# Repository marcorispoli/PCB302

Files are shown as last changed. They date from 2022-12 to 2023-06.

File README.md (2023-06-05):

# PCB/22-302 - Compressor device controller (DiMoBIS)

## Descrizione

Scheda di controllo del dispositivo di compressione del mammografo Z190.

## Struttura cartelle

```text
pcb-22-302/     [pcb-22-302.git]
├── artifacts/
│   ├── archive/
│   ├── current/
│   │   ├── docs/
│   │   └── layout/
│   │       ├── drawings/
│   │       ├── gerbers/
│   │       └── pick&place/
│   ├── datasheets/
│   └── releases/
├── capture/
├── docs/
├── layout/
├── scripts/
└── spice/
```

- `artifacts` contiene tutti gli artefatti generati dal progetto ed eventuali risorse esterne.
  - `archive` contiene le versioni archiviate degli artefatti generati.
  - `current` contiene la versione corrente degli artefatti generati.
  - `datasheets` contiene la documentazione di alcuni componenti utilizzati nel progetto.
  - `releases` contiene i rilasci del progetto del master del PCB.
- `capture` contiene il progetto dello schematico.
- `docs` contiene la documentazione di progetto.
- `layout` contiene il progetto del layout del PCB.
- `scripts` contiene lo script di generazione della lista parti.
- `spice` contiene alcuni progetti di simulazione.

## Strumenti di sviluppo

- Lo schematico della scheda è sviluppato in **Cadence OrCAD Capture 17.4**.
- Il layout del PCB della scheda è sviluppato in **Cadence OrCAD Layout Plus 16.2**.

## Documentazione

- [Progettazione](docs/progettazione.md)
- [Schematico](artifacts/current/docs/SE22-302-0_r3.pdf)
- [Schematico (collaudo)](docs/collaudo-rev2.pdf)
- [Lista parti](artifacts/current/docs/LP22-302-0_r3.pdf)
- [Piano di montaggio](artifacts/current/layout/drawings/PM22-302-0.pdf)

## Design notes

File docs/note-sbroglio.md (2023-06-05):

# Note di sbroglio

*Ultima modifica: 31/05/2023*

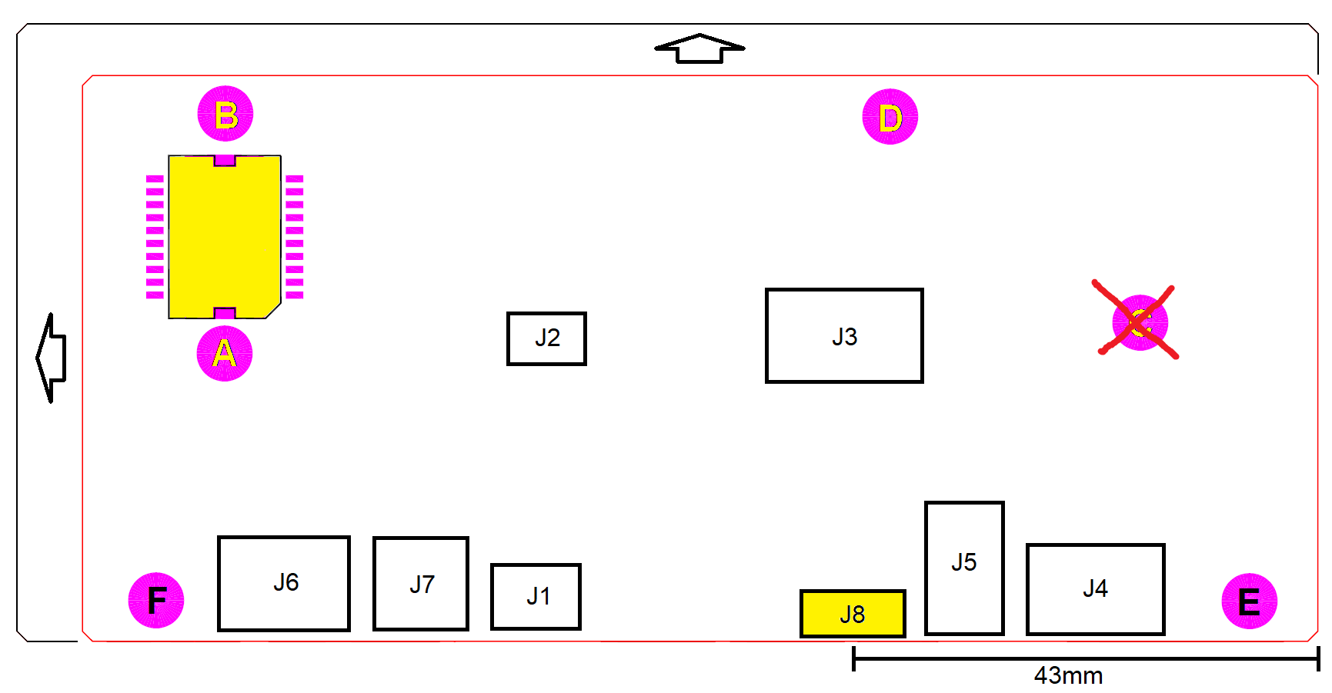
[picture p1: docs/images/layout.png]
layout


1. Il codice del circuito stampato è **CS/22-302-0**.

2. La struttura della scheda ricalca grosso modo quella della scheda 16-269-0. La serigrafia della nuova scheda sarà ruotata di 180° rispetto alla scheda 16-269-0.

3. Le dimensioni minime della scheda sono uguali a quelle della scheda 16-269-0, `121.3mm x 55.6mm` (contorno rosso), le dimensioni massime sono `130mm x 60mm` (contorno nero). L'estensione può avvenire verso sinistra e verso l'alto.

4. Il PCB ha spessore 1.6mm ed ha 4 strati.

5. La foratura della scheda 16-269-0 è rappresentata dai fori **A**, **B**, **C** e **D**. Nella nuova scheda verrà rimosso il foro **C** e si aggiungeranno i fori **E** e **F** posizionati lungo il bordo inferiore, ai lati dei connettori.

6. I connettori sono di seguito elencati:

    | Connettore | Etichetta | Tipo         | Descrizione                          |
    | -- | ------------- | ---------------- | ------------------------------------ |
    | J1 | `24VDC`       | [105311-1102]    | Alimentazione a 24V                  |
    | J2 | `SUPPLY_TEST` | [HEADER-3x2]     | Monitor alimentazioni scheda         |
    | J3 | `DEBUG`       | [61200621621]    | Interfaccia di programmazione        |
    | J4 | `HW_BUS`      | [105310-2210]    | Interfaccia Hardware Bus             |
    | J5 | `POSITION`    | [22-05-3031]     | Interfaccia  potenziometro posizione |
    | J6 | `MOTOR`       | [MC1,5/3-G-3,81] | Interfaccia motore                   |
    | J7 | `BRAKE`       | [MC1,5/2-G-3,81] | Interfaccia freno                    |
    | J8 | `PADDLE`      | [54548-1071]     | Interfaccia paddle                   |

    [105311-1102]: https://www.molex.com/pdm_docs/sd/1053111102_sd.pdf
    [61200621621]: https://www.we-online.com/catalog/datasheet/61200621621.pdf
    [105310-2210]: https://www.molex.com/pdm_docs/sd/1053101210_sd.pdf
    [22-05-3031]: https://www.molex.com/pdm_docs/sd/022053031_sd.pdf
    [MC1,5/3-G-3,81]: https://www.phoenixcontact.com/product/pdf/api/v1/MTgwMzI4MA?_realm=us&_locale=en-US&blocks=commercial-data%2Ctechnical-data%2Cdrawings
    [MC1,5/2-G-3,81]: https://www.phoenixcontact.com/product/pdf/api/v1/MTgwMzI3Nw?_realm=us&_locale=en-US&blocks=commercial-data%2Ctechnical-data%2Cdrawings
    [54548-1071]: https://www.molex.com/pdm_docs/sd/545482671_sd.pdf
    [HEADER-3x2]: https://www.molex.com/pdm_docs/sd/901310123_sd.pdf

7. I connettori **J1**, **J4**, **J5**, **J6**, **J7**, **J8** devono essere posizionati lungo il bordo inferiore della scheda.

8. Il connettore **J8** deve essere posizionato a 43mm (asse simmetria) dal bordo destro della scheda.

9. Il piano di massa **GND** deve essere solido e continuo, a meno eventualmente della net **CHASSIS_GND**.

10. I diodi TVS (**SMBJ\*A**, **SD05-\***) devono essere piazzati il più vicino possibile ai connettori associati.

11. La net **CHASSIS_GND**, (copper area?) deve essere posizionata lungo tutto il bordo inferiore e accogliere tutti gli anodi dei diodi TVS.

12. I fori **E** ed **F** devono essere connessi alla net **CHASSIS_GND** così come indicato nello schematico dai fori **MH1** e **MH2**. Il foro **MH1** sarà connesso a **GND** tramite **R6** il più vicino possibile al foro.

13. Riportare sulla serigrafia le etichette espresse dalla proprietà **COMMENT** dei componenti dello schematico, limitatamente ai connettori, ai testpoint e ai led. NON INCLUDERE LE PARENTESI QUADRE.

14. Piazzare i led sullo strato TOP.

## Modifiche sbroglio (schematico revisione 3)

[Collaudo revisione 2](./collaudo-rev2.pdf)

- [x] Portare i connettori **J6** (`MOTOR`) e **J7** (`BRAKE`) a filo del bordo scheda. Spostare le etichette all'interno.
- [x] Scambiare di posto **DL12** e **DL13**.
- [x] Riportare in visibilità l'etichetta di **R41**, coperta dal solder mask di **U11**.
- [x] Inserito **R78** sulla net `CURRENT_SENSOR`, nella pagina `ANALOG`.
- [x] Inserito **R79** in parallelo a **C37**, nella pagina `MOTOR`.
- [x] Corretto il simbolo sullo schematico di **U12**.
- [x] Invertite le net sui pin `1` e `2` di **U12**.
- [x] Inserito il jumper **J9** in parallelo all'uscita di **U12**, nella pagina `MOTOR`.
- [x] Inserito **D29** in parallelo a **J7**, nella pagina `BRAKE`.
- [x] Disconnesso il pin `11` di **U13** e **U14** dalla net `CALIBRATION_ENA`, nella pagina `SAFETY1`.
- [x] Inseriti **D30** e **R80** sull'ingresso di **U16A**, nella pagina `SAFETY2`.
- [x] Sostituito il connettore **J8** con connettore da 12 pin anziché 10, nella pagina `PADDLE`.
- [x] Il codice `22-302-0` resta invariato.

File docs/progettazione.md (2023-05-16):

# PCB/22-302 - Progettazione

- [1. Requisiti](#1-requisiti)
  - [1.1. Alimentazione](#11-alimentazione)
  - [1.2. Elaborazione](#12-elaborazione)
  - [1.3. Comunicazione](#13-comunicazione)
  - [1.4. Azionamento](#14-azionamento)
  - [1.5. Gestione paddle](#15-gestione-paddle)
  - [1.6. Sicurezza](#16-sicurezza)
- [2. Implementazione](#2-implementazione)
  - [2.1. Dispositivi](#21-dispositivi)
    - [2.1.1. Motore](#211-motore)
    - [2.1.2. Freno di tenuta](#212-freno-di-tenuta)
    - [2.1.3. Sensore di forza](#213-sensore-di-forza)
    - [2.1.4. Potenziometro](#214-potenziometro)
  - [2.2. Connettori](#22-connettori)
  - [2.3. Alimentazione](#23-alimentazione)
  - [2.4. Processore](#24-processore)
    - [2.4.1. Revisione della scheda](#241-revisione-della-scheda)
  - [2.5. Comunicazione](#25-comunicazione)
    - [2.5.1. Interfaccia `HW_BUS`](#251-interfaccia-hw_bus)
    - [2.5.2. Interfaccia `PADDLE`](#252-interfaccia-paddle)
  - [2.6. Azionamento](#26-azionamento)
    - [2.6.1. Motore](#261-motore)
    - [2.6.2. Freno di tenuta](#262-freno-di-tenuta)
    - [2.6.3. Sensore di forza](#263-sensore-di-forza)
    - [2.6.4. Sensore di posizione](#264-sensore-di-posizione)
    - [2.6.5. Sensore di corrente](#265-sensore-di-corrente)
  - [2.7. Sicurezza](#27-sicurezza)
    - [2.7.1. Potenziometri](#271-potenziometri)
    - [2.7.2. Comparatori](#272-comparatori)
    - [2.7.3. Abilitazione della calibrazione](#273-abilitazione-della-calibrazione)
    - [2.7.4. Abilitazione del compressore](#274-abilitazione-del-compressore)
    - [2.7.5. Rilevazione della compressione](#275-rilevazione-della-compressione)
    - [2.7.6. Blocco della compressione](#276-blocco-della-compressione)
    - [2.7.7. Taglio dell'alimentazione del motore](#277-taglio-dellalimentazione-del-motore)
- [3. Documentazione](#3-documentazione)
  - [3.1. Componenti](#31-componenti)

## 1. Requisiti

Di seguito sono descritti tutti i requisiti a cui la progettazione della scheda PCB/22-302 è chiamata a soddisfare, così come sono stati definiti all'interno della documentazione qui sotto elencata:

- *Gantry Hardware Specification - Compressor Device*
- *Gantry Hardware Specification - Hardware Interfaces*

### 1.1. Alimentazione

La scheda PCB/22-302 riceve un'alimentazione in tensione continua a 24V direttamente dalla scheda servizi PCB/22-301, che ne garantisce la continuità tramite la funzione UPS.

### 1.2. Elaborazione

Le funzioni di controllo del compressore sono eseguite dalla scheda PCB/22-302 per mezzo di un microcontrollore a 32 bit, modello SAME51J20A, prodotto da Microchip, avente core ARM Cortex-M4 a 120MHz, e package TQFP a 64 pin.

### 1.3. Comunicazione

La scheda PCB/22-302 comunica con il sistema di elaborazione centrale, rappresentato dal *Gantry Control Unit*, per mezzo del *CAN Bus* a 1Mbps.

La scheda PCB/22-302 è inoltre connessa all'*Hardware Bus* proveniente dalla scheda PCB/22-305 (C-ARM Hub).

### 1.4. Azionamento

L'azionamento del compressore viene realizzato tramite il controllo di un motore a spazzole in corrente continua che movimenta il paddle di compressione, su un binario di scorrimento, per mezzo di una cinghia dentata.

Il controllo dell'azionamento è coadiuvato da un sensore di forza posto sul supporto del paddle e da un sensore potenziometrico che restituisce la posizione del carrello del paddle sul binario.

L'azionamento del compressore è comandato in vari modi:

- tramite comandi ricevuti dal *Gantry Control Unit* attraverso il *CAN Bus*;
- tramite appositi segnali dell'*Hardware Bus*;
- tramite interruttori incorporati nelle manopole per la compressione manuale ed integrate nel supporto del paddle.

### 1.5. Gestione paddle

Il paddle di compressione è un componente estraibile e sostituibile con diversi modelli. Il sistema deve conoscere se il paddle è presente e che tipo di paddle è installato.

L'elettronica di rilevamento e identificazione del paddle è situata sulla scheda PCB/22-306 (Paddle Device Board). Su tale scheda sono inoltre connessi il sensore di forza e i pulsanti di attivazione manuale integrati nelle manopole del compressore.

La scheda PCB/22-306 è connessa alla scheda PCB/22-302 e da questa riceve l'alimentazione.

### 1.6. Sicurezza

L'azionamento del motore del compressore deve tenere in conto l'informazione della pressione realizzata durante l'azionamento stesso.

La massima compressione realizzabile per via automatica, cioè eseguita dal firmware controllando il motore, è limitata a 200N. Tale limite deve essere garantito da un'opportuna elettronica, posta al di fuori del controllo del firmware, che impedisca ulteriori aumenti della pressione pur consentendo la decompressione.

Oltre l'azionamento automatico fino a un massimo di 200N, il sistema prevede l'intervento manuale per l'incremento della compressione fino a 300N. Anche questo secondo limite deve essere garantito dall'elettronica non controllata dal firmware e, in caso di violazione, deve provvedere al taglio completo della potenza dell'azionamento.

## 2. Implementazione

### 2.1. Dispositivi

#### 2.1.1. Motore

| Proprietà   | Valore                             |
| ----------- | ---------------------------------- |
| Produttore  | Soho Precision Machinery Co., Ltd. |
| Part number | `GBN50-4D-25068B-28Y-RC-RH`        |
| Codice MT   | MR-GBN50-4D-2                      |

- [SOHO homepage](http://sohomotor.com/index.html)
- [DC Gearmotors](../artifacts/datasheets/motore/soho/Compact-DC-Gearmotors-Product-Data-Sheet_v2.pdf)
- [7E4065B-28Y (DC Motor)](../artifacts/datasheets/motore/soho/7E4065.pdf)
- [GBN50 (Spur Gearhead)](../artifacts/datasheets/motore/soho/GBN50.pdf)

#### 2.1.2. Freno di tenuta

#### 2.1.3. Sensore di forza

| Proprietà   | Valore               |
| ----------- | -------------------- |
| Produttore  | TE Connectivity      |
| Part number | `FX293X-100A-0100-L` |
| Codice MT   | ???                  |

- [Product page](https://www.te.com/usa-en/product-CAT-FSE0006.html)
- [Datasheet](../artifacts/datasheets/sensore/te/FX29.pdf)

#### 2.1.4. Potenziometro

| Proprietà   | Valore         |
| ----------- | -------------- |
| Produttore  | Bourns         |
| Part number | `3590S-2-502L` |
| Codice MT   | ???            |

- [Product page](https://www.bourns.com/products/potentiometers/precision-pots-multiturn/product/3590)
- [Datasheet](../artifacts/datasheets/potenziometro/3590.pdf)

### 2.2. Connettori

| Connettore | Etichetta | Tipo         | Descrizione                          |
| -- | ------------- | ---------------- | ------------------------------------ |
| J1 | `24VDC`       | [105311-1102]    | Alimentazione a 24V                  |
| J2 | `SUPPLY_TEST` | [HEADER-3x2]     | Monitor alimentazioni scheda         |
| J3 | `DEBUG`       | [61200621621]    | Interfaccia di programmazione        |
| J4 | `HW_BUS`      | [105310-2210]    | Interfaccia Hardware Bus             |
| J5 | `POSITION`    | [22-05-3031]     | Interfaccia  potenziometro posizione |
| J6 | `MOTOR`       | [MC1,5/3-G-3,81] | Interfaccia motore                   |
| J7 | `BRAKE`       | [MC1,5/2-G-3,81] | Interfaccia freno                    |
| J8 | `PADDLE`      | [54548-1071]     | Interfaccia paddle                   |

[105311-1102]: https://www.molex.com/pdm_docs/sd/1053111102_sd.pdf
[61200621621]: https://www.we-online.com/catalog/datasheet/61200621621.pdf
[105310-2210]: https://www.molex.com/pdm_docs/sd/1053101210_sd.pdf
[22-05-3031]: https://www.molex.com/pdm_docs/sd/022053031_sd.pdf
[MC1,5/3-G-3,81]: https://www.phoenixcontact.com/product/pdf/api/v1/MTgwMzI4MA?_realm=us&_locale=en-US&blocks=commercial-data%2Ctechnical-data%2Cdrawings
[MC1,5/2-G-3,81]: https://www.phoenixcontact.com/product/pdf/api/v1/MTgwMzI3Nw?_realm=us&_locale=en-US&blocks=commercial-data%2Ctechnical-data%2Cdrawings
[54548-1071]: https://www.molex.com/pdm_docs/sd/545482671_sd.pdf
[HEADER-3x2]: https://www.molex.com/pdm_docs/sd/901310123_sd.pdf

### 2.3. Alimentazione

L'alimentazione viene fornita alla scheda tramite il connettore **J1** (`24VDC`):

| Pin | Segnale | Descrizione         |
| - | -------- | -------------------- |
| 1 | `IN_24V` | Ingresso linea a 24V |
| 2 | `IN_0V`  | Ingresso linea a 0V  |

L'alimentazione in ingresso viene posta in protezione tramite un fusibile **F1** da 5A, e filtrata con il filtro EMI **FLT1**, fornendo alla scheda la net di alimentazione `24V`.

A partire dall'alimentazione `24V`, tramite il regolatore switching **U1** ([R-78E-1.0]), viene generata l'alimentazione `5V`, per una corrente fino a 1A.

Dall'alimentazione `5V`, tramite il regolatore lineare **U2** ([NCP1117]), viene generata l'alimentazione `3V3`, per una corrente fino a 1A.

Le tre alimentazioni fornite alla scheda sono riportate sul connettore **J2** (`SUPPLY_TEST`) per agevolarne il test. Un partitore con rapporto 1:12 e applicato all'alimentazione `24V` produce il segnale `SUPPLY_MONITOR` in ingresso al microcontrollore.

### 2.4. Processore

Di seguito l'elenco dei segnali gestiti dal processore **U3** ([SAME51J20A]):

| Segnale           | Tipo | Direzione | Descrizione                                                   |
| ----------------- | :-------: | :--: | ------------------------------------------------------------- |
| `SUPPLY_MONITOR`  | analogico | I    | Partitore 1:12 dell'alimentazione `24V`                       |
| `COMPRESSOR_ENA`  | digitale  | I    | Abilitazione del compressore dall'HW_BUS                      |
| `COMPRESSOR_UP`   | digitale  | I    | Comando di decompressione dall'HW_BUS                         |
| `COMPRESSOR_DOWN` | digitale  | I    | Comando di compressione dall'HW_BUS                           |
| `CALIBRATION_ENA` | digitale  | I    | Abilitazione della calibrazione dall'HW_BUS                   |
| `BRIDGE_IN1`      | digitale  | O    | Controllo dell'half bridge 1 del driver motore                |
| `BRIDGE_IN2`      | digitale  | O    | Controllo dell'half bridge 2 del driver motore                |
| `BRIDGE_ENB`      | digitale  | O    | Abilitazione del driver motore                                |
| `BRIDGE_ENB_FB`   | digitale  | I    | Feedback dell'abilitazione del driver motore                  |
| `BRAKE_OFF`       | digitale  | O    | Comando di distacco del freno di tenuta                       |
| `MOTOR_CUT`       | digitale  | O    | Comando di interruzione dell'alimentazione del motore         |
| `CURRENT_SENSOR`  | analogico | I    | Segnale del sensore di corrente del motore                    |
| `POSITION_SENSOR` | analogico | I    | Segnale del sensore di posizione                              |
| `FORCE_SENSOR`    | analogico | I    | Segnale del sensore di forza                                  |
| `FORCE_OVF1`      | digitale  | I    | Overflow della 1° soglia del sensore di forza                 |
| `FORCE_OVF2`      | digitale  | I    | Overflow della 2° soglia del sensore di forza                 |
| `FORCE_OVF3`      | digitale  | I    | Overflow della 3° soglia del sensore di forza                 |
| `CURRENT_OVF`     | digitale  | I    | Overflow della soglia del picco di corrente del motore        |
| `PADDLE_PRESENT`  | digitale  | I    | Segnale di presenza paddle                                    |
| `PADDLE_UP`       | digitale  | I    | Comando di decompressione dalla scheda PADDLE                 |
| `PADDLE_DOWN`     | digitale  | I    | Comando di compressione dalla scheda PADDLE                   |
| `UART_RX`         | digitale  | I    | Linea di ricezione dell'UART connessa con la scheda PADDLE    |
| `UART_TX`         | digitale  | O    | Linea di trasmissione dell'UART connessa con la scheda PADDLE |
| `CAN_RX`          | digitale  | I    | Linea di ricezione del CAN bus                                |
| `CAN_TX`          | digitale  | O    | Linea di trasmissione del CAN bus                             |
| `I2C_SDA`         | digitale  | I/O  | Linea dati del bus I2C                                        |
| `I2C_SCL`         | digitale  | O    | Linea di clock del bus I2C                                    |
| `ACTIVITY`        | digitale  | O    | Controllo del led **DL4** (`CPU`)                             |
| `HW_REVISION`     | analogico | I    | Revisione della scheda                                        |

#### 2.4.1. Revisione della scheda

L'informazione della revisione della scheda è fornita al microcontrollore dal partitore {**R12**, **R13**} le cui resistenze variano a passi di $500\Omega$ e la cui somma è fissa a $4k\Omega$. In tal modo:

$$ V_{HW\_REVISION} = 3.3V * \frac{n}{8} \space,\space con \space 0 \le n \le 8 $$

### 2.5. Comunicazione

La scheda PCB/22-302 comunica con l'esterno attraverso i connettori **J4** (`HW_BUS`) e **J8** (`PADDLE`).

#### 2.5.1. Interfaccia `HW_BUS`

Il connettore **J4** fornisce le interfacce dell'hardware bus, propriamente detto, e del CAN Bus.

| Pin | Segnale        | Pin | Segnale     |
| --- | -------        | --- | ----------- |
| 1   | `HW_CAN_H`     | 6   | `HW_CAN_L`  |
| 2   | `HW_CAN_GND`   | 7   | nc          |
| 3   | `HW_CMP_ENA`   | 8   | `HW_CMP_UP` |
| 4   | `HW_CMP_DWN`   | 9   | `HW_CMP_ON` |
| 5   | `HW_CALIB_ENA` | 10  | `GND_HW`    |

Segue la descrizione dei segnali:

- `HW_CAN_H`     - \[I/O\] Linea dati alta del CAN bus
- `HW_CAN_L`     - \[I/O\] Linea dati bassa del CAN bus
- `HW_CAN_GND`   - Massa del CAN bus
- `HW_CMP_ENA`   - \[I\] Abilitazione dell'azionamento del compressore. E' utilizzato dal microcontrollore ma interviene anche direttamente sull'hardware di azionamento.
- `HW_CMP_UP`    - \[I\] Richiesta di decompressione. E' utilizzato dal solo microcontrollore.
- `HW_CMP_DWN`   - \[I\] Richiesta di compressione. E' utilizzato dal solo microcontrollore.
- `HW_CMP_ON`    - \[O\] Stato di compressione in essere. Viene attivato quando il sensore di forza rileva una forza superiore ad un'appropriata soglia. **Viene generato per via hardware**.
- `HW_CALIB_ENA` - \[I\] Abilitazione delle operazioni di calibrazione. Interviene direttamente sull'hardware di calibrazione.
- `GND_HW`       - Massa dell'hardware bus

I segnali `HW_CAN_H`, `HW_CAN_L` e `HW_CAN_GND` sono inoltrati verso il driver **U4** ([TJA1050T]) che fornisce al processore i segnali `CAN_TX` e `CAN_RX`.

I restanti segnali dell'hardware bus, di dinamica compresa in 5V, sono isolati otticamente, tramite **U5**, **U6**, **U7**, **U8** e **U9** ([TCMT1103] e [CPC1017N]), e accoppiati ai segnali della scheda `COMPRESSOR_ENA`, `COMPRESSOR_UP`, `COMPRESSOR_DOWN`, `CALIBRATION_ENA` e `FORCE_OVF1`,

Di seguito il dimensionamento delle polarizzazioni degli opto-isolatori.

- TCMT1103: $V_F = 1.2V$, $CTR = 100\% \div 200\%$ ($@ I_F = 10mA$)
- CPC1017N: $V_F = 1.2V$, $R_{ON} = 6.5\Omega$ ($@ I_F = 5mA$)

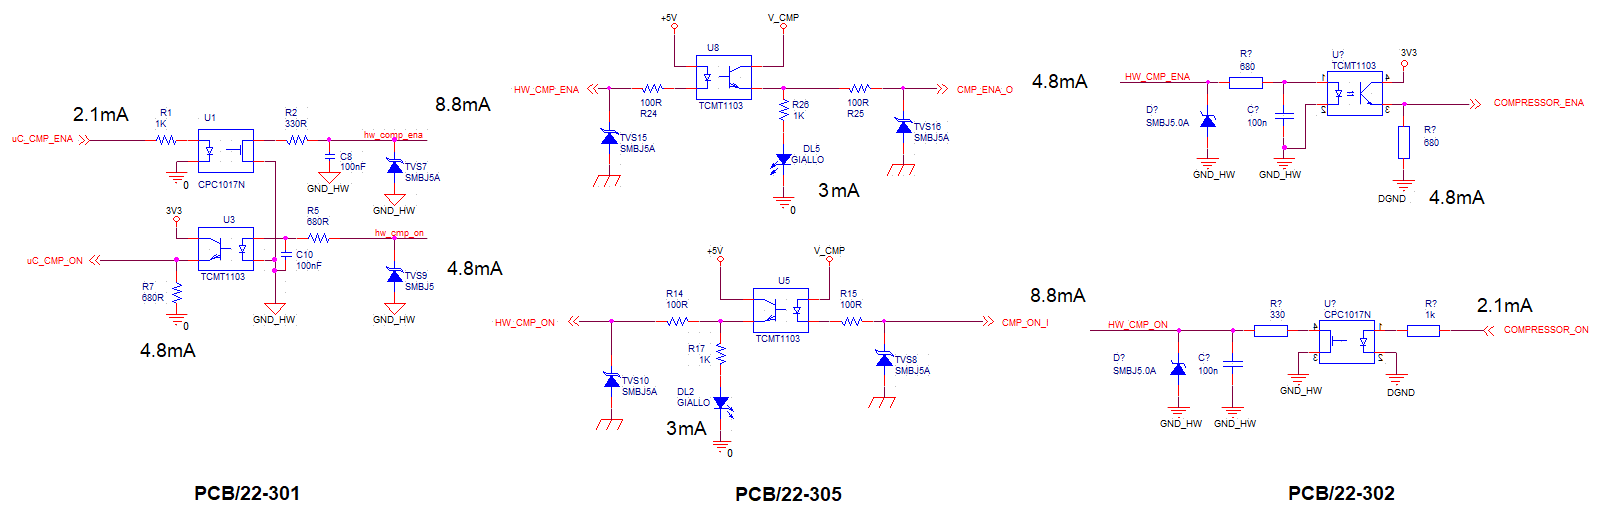
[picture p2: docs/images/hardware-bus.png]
hardware-bus


#### 2.5.2. Interfaccia `PADDLE`

Il connettore **J8** fornisce l'interfaccia verso la scheda PCB/22-306 (Paddle Device Board).

| Pin | Segnale        | Descrizione                                                        |
| --- | -------------- | ------------------------------------------------------------------ |
| 1   | `PAD_DVDD`     | Alimentazione a 5V della sezione digitale della scheda PCB/22-306  |
| 2   | `PAD_DGND`     | Massa della sezione digitale della scheda PCB/22-306               |
| 3   | `PAD_RX`       | \[O\] Linea di ricezione del lettore RFID                          |
| 4   | `PAD_TX`       | \[I\] Linea di trasmissione del lettore RFID                       |
| 5   | `PAD_PRESENT`  | \[I\] Presenza del paddle                                          |
| 6   | `PAD_UP`       | \[I\] Comando di decompressione                                    |
| 7   | `PAD_DOWN`     | \[I\] Comando di compressione                                      |
| 8   | `PAD_AVDD`     | Alimentazione a 5V della sezione analogica della scheda PCB/22-306 |
| 9   | `PAD_AGND`     | Massa della sezione analogica della scheda PCB/22-306              |
| 10  | `PADDLE_FORCE` | \[A\] Sensore di forza                                             |

I segnali digitali dell'interfaccia sono controllati nei loro fronti di salita allo scopo di limitare le emissioni attraverso il cablaggio verso la scheda PCB/22-306. A tale scopo le uscite sono filtrate attraverso un passa-basso RC con costante di tempo pari a 10us, mentre gli ingressi sono applicati al driver **U17** ([SN74HCS365]) con funzione di trigger di Schmidt al fine di ripristinare una veloce transizione dei segnali inoltrati verso il processore. La stessa procedura dovrà essere adottata sull'altro lato del cablaggio, cioè sulla scheda PCB/22-306.

### 2.6. Azionamento

L'azionamento del compressore viene realizzato per il tramite di un motore a spazzole in corrente continua controllato dal processore **U3** usando le informazioni fornite dai sensori di forza, di posizione e di corrente. In fase si arresto il motore è bloccato da un freno di tenuta.

#### 2.6.1. Motore

Il connettore **J6** (`MOTOR`) connette il motore al driver **U11** ([L6205PD]):

| Pin | Segnale | Descrizione             |
| --- | ------- | ----------------------- |
| 1   | `MOT1`  | Terminale 1 del motore  |
| 2   | -       | -                       |
| 3   | `MOT2`  | Terminale 2 del motore  |

Il driver **U11** contiene due ponti H completi (**A** e **B**) ed è configurato in modo che i semi-ponti del ponte **A** sono collegati in parallelo tra loro; lo stesso vale per il ponte **B**.

In tal modo il driver **U11** fornisce un ponte H completo con le seguenti caratteristiche:

- $R_{DS(ON)}$ : $0.15\Omega$
- Max RMS load current : $2.8A$
- OCD threshold : $5.6A$

I limiti di corrente corrispondono a quelli del singolo ponte H, ma la resistenza equivalente è dimezzata, consentendo una minore dissipazione di potenza.

Il modello di dissipazione è rappresentato dalla relazione

$$\ P_D = 2 \cdot R_H \cdot I_H^2 $$

dove

- $R_H$ rappresenta la resistenza equivalente del semi-ponte, comprensiva della quota di dissipazione dinamica, che ha un valore di circa $1.25\Omega$.
- $I_H$ rappresenta la corrente nel semi-ponte.

Ipotizzando una corrente massima nel motore pari a $I_{M,max}=1.5A$, la corrente in ciascun semi-ponte è pari alla metà di tale corrente, perciò

$$ P_{D,max} = 2 \cdot 1.25\Omega \cdot \left(\frac{1.5A}{2}\right)^2 = 1.4W $$

Il driver **U11** è provvisto di una piastrina di dissipazione (slug) nella faccia inferiore del contenitore. La resistenza termica tra giunzione e ambiente $R_{th,j-amb}$ può essere considerata compresa tra i valori:

- $30°C/W$ con lo slug saldato sul top e connesso da 16 vie al piano di massa, senza ulteriori aree di dissipazione.
- $62°C/W$ con lo slug non saldato.

La dissipazione della potenza massima $P_{M,max}$ comporta un innalzamento della temperatura di giunzione, rispetto all'ambiente, pari a:

$$ 42°C \lt \Delta T_{j-amb} \lt 87°C $$

comunque compatibile con i limiti del dispositivo.

Il driver **U11** è controllato dal processore per mezzo dei seguenti segnali:

| Segnale         | Descrizione                           |
| --------------- | ------------------------------------- |
| `BRIDGE_ENB_S`  | Abilitazione del driver               |
| `BRIDGE_ENB_FB` | Feedback dell'abilitazione del driver |
| `BRIDGE_IN1`    | Controllo del semi-ponte 1            |
| `BRIDGE_IN2`    | Controllo del semi-ponte 2            |

Il driver **U11** implementa la protezione contro la sovraccorrente. In caso di superamento della soglia $I_{OCD}$, l'abilitazione del driver viene forzata a massa, interrompendo l'alimentazione del motore. Il segnale `BRIDGE_ENB_FB` segnala tale evenienza al processore.

#### 2.6.2. Freno di tenuta

Il freno di tenuta resta bloccato fintanto che non viene alimentato. Il processore provvede a fornirgli la necessaria alimentazione tramite il segnale `BRAKE_OFF_S` che attiva il transistor **Q11**, sbloccando così il motore del compressore.

#### 2.6.3. Sensore di forza

Il sensore di forza è montato sulla scheda PCB/22-306 e fornisce la sua informazione attraverso l'interfaccia `PADDLE`. Il segnale `PADDLE_FORCE` fornito dal sensore ha una dinamica compresa tra 0.5V e 4.5V per valori della forza misurata compresi tra 0N e 500N.

Il segnale viene applicato ad un inseguitore di tensione e ridotto da un partitore con rapporto 2:3 per fornire al processore il segnale `FORCE_SENSOR`, la cui dinamica risulta quindi compresa tra 0.33V e 3V.

#### 2.6.4. Sensore di posizione

Il sensore di posizione è realizzato attraverso un potenziometro multigiri alimentato a 5V. Il segnale proveniente dal potenziometro viene applicato ad un inseguitore di tensione e ridotto da un partitore con rapporto 2:3 per fornire al processore il segnale `POSITION_SENSOR` avente dinamica compresa tra 0V e 3V.

#### 2.6.5. Sensore di corrente

Il sensore di corrente restituisce l'informazione della corrente che scorre all'interno del motore. Tale misura è utile a verificare l'informazione proveniente dal sensore di forza. Essendo infatti la coppia esercitata dal motore strettamente legata alla corrente che in esso scorre, il sensore di corrente rappresenta una preziosa ridondanza per il sensore di forza.

La misura parte dalla tensione `BRIDGE_SENS` presente ai capi della resistenza **R41** da $0.1\Omega/2W$, posta in serie al ponte H realizzato dal driver **U11** e collegata a massa.

Per una corrente massima di $I_{M,max}=1.5A$ la massima caduta di tensione su **R41** corrisponde a $V_{BRIDGE\_SENS,max}=150mV$, inoltre la massima dissipazione sarebbe $P_{R1,max}=225mW$, per cui una resistenza di $0.5W$ sarebbe stata sufficiente.

Il segnale `BRIDGE_SENS` viene filtrato (passa-basso RC con $\tau=100ns$) e amplificato con guadagno 10 per fornire al processore il segnale `CURRENT_SENSOR` avente massima dinamica di 1.5V.

Il segnale `CURRENT_SENSOR` viene inoltre applicato ad un rivelatore di picco la cui uscita `CURRENT_PEAK` viene utilizzata per la realizzazione di una sicurezza. Il rivelatore di picco presenta una costante di tempo per la carica pari a $\tau_c=10us$ e una costante di tempo per la scarica pari a $\tau_s=4ms$.

### 2.7. Sicurezza

Nella scheda sono implementate un numero di misure di sicurezza volte a ridurre l'impatto di eventuali condizioni di anomalia dovute principalmente a malfunzionamenti del firmware in esecuzione sul processore. A tale scopo queste sicurezze sono realizzate tramite soluzioni puramente hardware senza il coinvolgimento del processore.

Le sicurezze implementate sono governate essenzialmente dalle abilitazioni provenienti dall'hardware bus e da appositi comparatori che mettono a confronto le informazioni di forza e di corrente con soglie opportunamente configurate tramite potenziometri.

#### 2.7.1. Potenziometri

I potenziometri digitali **U13** e **U14** forniscono quattro soglie di tensione `VREF1`, `VREF2`, `VREF3` e `VREF4` comprese tra 0V e 3.3V.

Tali potenziometri sono controllati dal processore tramite il bus I2C. Di seguito sono indicati gli indirizzi sul bus dei due dispositivi:

| Dispositivo | Indirizzo bus I2C |
| --- | ---------- |
| U13 | `0101000b` |
| U14 | `0101001b` |

#### 2.7.2. Comparatori

Sulla scheda sono implementati quattro comparatori con isteresi. Tre di essi mettono a confronto il segnale `FORCE_SENSOR` con le soglie `VREF1`, `VREF2` e `VREF3` fornendo i segnali `FORCE_OVF1`, `FORCE_OVF2` e `FORCE_OVF3`. Il quarto comparatore confronta il segnale `CURRENT_PEAK` con la quarta soglia `VREF4` restituendo il segnale `CURRENT_OVF`.

I comparatori sono configurati per esprimere un'isteresi pari a 33mV, cioè pari a 1/100 della dinamica di alimentazione.

Di seguito la raffigurazione di un comparatore non invertente con isteresi:

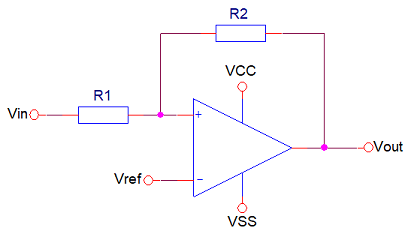
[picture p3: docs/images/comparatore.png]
comparatore


A causa della reazione positiva si hanno due configurazioni stabili equivalenti:

1. La tensione sull'ingresso non invertente $V^+$ dell'opamp è **superiore** alla tensione di riferimento $V_{ref}$, comportando in uscita dell'opamp una tensione pari a $V_{CC}$.
2. La tensione sull'ingresso non invertente $V^+$ dell'opamp è **inferiore** alla tensione di riferimento $V_{ref}$, comportando in uscita dell'opamp una tensione pari a $V_{SS}$.

Di seguito gli schemi equivalenti delle due configurazioni:

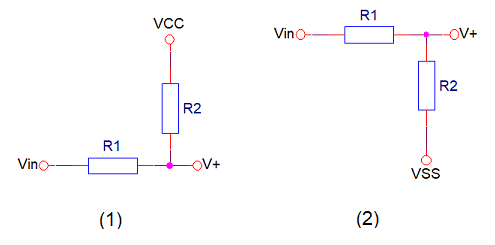
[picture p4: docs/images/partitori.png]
partitori


Il passaggio tra le due configurazioni si ha quando $V_{in}$ è tale che $V^+=V_{ref}$.

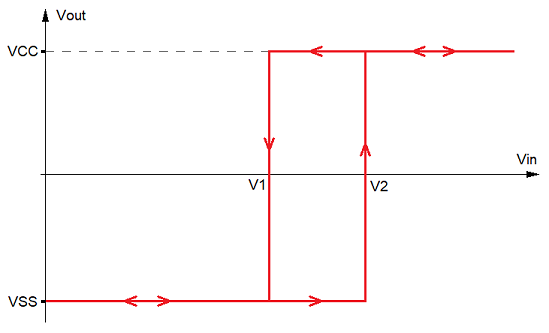
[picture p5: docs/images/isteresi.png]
isteresi


Dalla prima configurazione, posto $V_{in}=V_1$, si ha:

$$ V^+ = V_{ref} $$

$$ V_1 + (V_{CC} - V_1) \frac{R_1}{R_1 + R_2} = V_{ref} $$

mentre dalla seconda configurazione, posto $V_{in}=V_2$, si ha:

$$ V^+ = V_{ref} $$

$$ V_{SS} + (V_2 - V_{SS}) \frac{R_2}{R_1 + R_2} = V_{ref} $$

Semplificando rispetto a $V_{ref}$ si ottiene:

$$ V_1 + (V_{CC} - V_1) \frac{R_1}{R_1 + R_2} = V_{SS} + (V_2 - V_{SS}) \frac{R_2}{R_1 + R_2} $$

$$ V_1(R_1 + R_2) + (V_{CC} - V_1)R_1 = V_{SS}(R_1 + R_2) + (V_2 - V_{SS})R_2 $$

$$ V_1R_1 + V_1R_2 + V_{CC}R_1 - V_1R_1 = V_{SS}R_1 + V_{SS}R_2 + V_2R_2 - V_{SS}R_2 $$

$$ V_1R_2 + V_{CC}R_1 = V_{SS}R_1 + V_2R_2 $$

$$ (V_{CC} - V_{SS})R_1 = (V_2 - V_1)R_2 $$

La larghezza di isteresi è quindi pari a:

$$ \Delta V = V_2 - V_1 = (V_{CC} - V_{SS})\frac{R_1}{R_2} $$

#### 2.7.3. Abilitazione della calibrazione

I potenziometri digitali hanno memoria non volatile e devono essere programmati in una apposita procedura di calibrazione. Allo scopo di impedire indebiti accessi da parte del processore durante il normale funzionamento applicativo, il segnale `CALIBRATION_ENA` fornito dall'interfaccia `HW_BUS` controlla l'accesso ai potenziometri. Se infatti tale segnale non è attivo, è attiva la protezione contro la scrittura dei dispositivi ($\overline{WP}=low$). Inoltre se `CALIBRATION_ENA` è inattivo, la linea `I2C_SCL` è forzata a massa tramite i transistor **Q12** e **Q13** (pagina SAFETY1).

#### 2.7.4. Abilitazione del compressore

Il controllo del motore e del freno di tenuta da parte del processore viene abilitato tramite il segnale `COMPRESSOR_ENA` proveniente dall'interfaccia `HW_BUS`. Se infatti tale segnale è basso i segnali `BRIDGE_ENB_S` e `BRAKE_OFF_S` sono forzati a massa tramite i transistor **Q14**, **Q15** e **Q16** (pagina SAFETY3).

#### 2.7.5. Rilevazione della compressione

La rilevazione di compressione in corso viene eseguita tramite la comparazione del segnale `FORCE_SENSOR` e la soglia `VREF1` opportunamente calibrata (pagina SAFETY2). Il segnale di uscita del comparatore `FORCE_OVF1` viene applicato al terminale `HW_CMP_ON` dell'interfaccia `HW_BUS` (pagina HARDWARE BUS).

#### 2.7.6. Blocco della compressione

La compressione gestita da firmware è limitata al raggiungimento dei 200N di forza. Una volta raggiunto tale valore il driver del motore viene bloccato nel verso della compressione ma resta attivo nel verso della decompressione.

Il raggiungimento del limite dei 200N viene rilevato tramite la comparazione del segnale `FORCE_SENSOR` e la soglia `VREF2` opportunamente calibrata (pagina SAFETY2). Il segnale di uscita del comparatore `FORCE_OVF2` viene applicato ai transitor **Q17** e **Q18** che forzano il segnale `BRIDGE_IN1_S` a 3.3V. In questa maniera il semi-ponte 1 del driver **U11** risulta bloccato nella accensione del lato alto non permettendo ulteriori azionamenti del motore nel verso della compressione (SAFETY3).

> Il cablaggio del motore sul connettore **J6** deve essere disegnato in maniera che il blocco del semi-ponte 1 effettivamente impedisca il movimento del motore nel verso della compressione e non il contrario.

#### 2.7.7. Taglio dell'alimentazione del motore

Come detto la compressione automatica è limitata a 200N, ma è consentita un'ulteriore compressione, eseguita manualmente su apposite manopole installate sul supporto del paddle. La compressione manuale è a sua volta limitata a 300N. Nel caso che fosse superato tale limite, l'alimentazione del motore sarebbe interrotta.

Anche qui, il raggiungimento del limite dei 300N viene rilevato tramite la comparazione del segnale `FORCE_SENSOR` e la soglia `VREF3` opportunamente calibrata (pagina SAFETY2). Il segnale di uscita del comparatore `FORCE_OVF3` viene applicato al circuito di interruzione dell'alimentazione del motore.

Il circuito di interruzione è implementato tramite il relè a stato solido **U12** ([CPC1916Y]) pilotato da un multi-vibratore bistabile composto dai transistor **Q8** e **Q9** (pagina MOTOR).

All'accensione della scheda, il multi-vibratore è forzato nello stato attivo tramite il condensatore **C37**. Esso viene disattivato dal segnale `FORCE_OVF3` tramite il transistor **Q6**, spegnendo il relè **U12** e disalimentando il motore. Per la riattivazione del multi-vibratore è necessario spegnere e riaccendere la scheda.

## 3. Documentazione

### 3.1. Componenti

**Optoelettronici**:

- Opto-isolatore : [TCMT1103]
- Relè stato solido : [CPC1017N]
- Relè stato solido : [CPC1916Y]

[TCMT1103]: https://www.vishay.com/docs/83510/tcmt1100.pdf
[CPC1017N]: https://www.ixysic.com/home/pdfs.nsf/www/CPC1017N.pdf/$file/CPC1017N.pdf
[CPC1916Y]: https://www.ixysic.com/home/pdfs.nsf/www/CPC1916Y.pdf/$file/CPC1916Y.pdf

**Attivi**:

- Diodo piccoli segnali : [1N4148WT]
- Diodo TVS 600W : [SMBJ5.0A, SMBJ5.0CA, SMBJ30A, SMBJ30CA][SMBJ]
- Diodo TVS 450W : [SD05-01FTG][SD05]
- Diodo LED giallo : [APT2012YC]
- Diodo LED verde : [APT2012SGC]
- Diodo LED blu : [APT2012QBC/D]
- Diodo LED rosso : [APT2012EC]
- Transistor N-MOSFET 220mA : [BSS138]
- Transistor N-MOSFET 1.3A : [ZXMS6004FF]
- Transistor P-MOSFET 180mA : [BSS84]

[1N4148WT]: https://www.diodes.com/assets/Datasheets/1N4148WT.pdf
[SMBJ]: https://www.littelfuse.com/~/media/electronics/datasheets/tvs_diodes/littelfuse_tvs_diode_smbj_datasheet.pdf.pdf
[SD05]: https://www.littelfuse.com/~/media/electronics/datasheets/tvs_diode_arrays/littelfuse_tvs_diode_array_sd_datasheet.pdf.pdf
[APT2012YC]: https://www.kingbrightusa.com/images/catalog/SPEC/APT2012YC.pdf
[APT2012SGC]: https://www.kingbrightusa.com/images/catalog/SPEC/APT2012SGC.pdf
[APT2012QBC/D]: https://www.kingbrightusa.com/images/catalog/SPEC/APT2012QBC-D.pdf
[APT2012EC]: https://www.kingbrightusa.com/images/catalog/SPEC/APT2012EC.pdf
[BSS138]: https://www.onsemi.com/pdf/datasheet/bss138-d.pdf
[BSS84]: https://www.onsemi.com/pdf/datasheet/bss84-d.pdf
[ZXMS6004FF]: https://www.diodes.com/assets/Datasheets/ZXMS6004FF.pdf

**Passivi**:

- Bobina d'arresto : [DLW32SH101XF2L]
- Fusibile : [SMD050F-2]
- Ferrite : [BLM18BD102SN1D]
- Quarzo : [ECS-.327-12.5-16-TR3]

[DLW32SH101XF2L]: https://www.murata.com/products/productdata/8804914298910/QFLC9127.pdf
[SMD050F-2]: https://www.littelfuse.com/~/media/electronics/product_specifications/resettable_ptcs/littelfuse_ptc_smd050f_2_product_specification.pdf.pdf
[BLM18BD102SN1D]: https://www.murata.com/en-us/products/productdata/8796738650142/ENFA0003.pdf
[ECS-.327-12.5-16-TR3]: https://ecsxtal.com/store/pdf/ECX-16.pdf

**Integrati**:

- Driver CAN bus : [TJA1050T]
- Driver motore : [L6205PD]
- CPU : [SAME51J20A]
- Regolatore 5V : [R-78E-1.0]
- Regolatore 3.3V : [NCP1117]
- Amplificatore operazionale : [MCP6004]
- Potenziometro digitale : [MCP4661]
- Driver trigger di Schmidt : [SN74HCS365]

[TJA1050T]: https://www.nxp.com/docs/en/data-sheet/TJA1050.pdf
[L6205PD]: https://www.st.com/content/ccc/resource/technical/document/datasheet/group1/7f/8a/6c/96/c8/24/49/f6/CD00002345/files/CD00002345.pdf/jcr:content/translations/en.CD00002345.pdf
[SAME51J20A]: https://ww1.microchip.com/downloads/en/DeviceDoc/SAM_D5x_E5x_Family_Data_Sheet_DS60001507G.pdf
[R-78E-1.0]: https://recom-power.com/pdf/Innoline/R-78E-1.0.pdf
[NCP1117]: https://www.onsemi.com/pdf/datasheet/ncp1117-d.pdf
[MCP6004]: https://ww1.microchip.com/downloads/en/DeviceDoc/MCP6001-1R-1U-2-4-1-MHz-Low-Power-Op-Amp-DS20001733L.pdf
[MCP4661]: https://ww1.microchip.com/downloads/aemDocuments/documents/OTH/ProductDocuments/DataSheets/22107B.pdf
[SN74HCS365]: https://www.ti.com/lit/ds/symlink/sn74hcs365.pdf

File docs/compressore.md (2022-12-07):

# Struttura compressore

La struttura del compressore può essere così rappresentata:

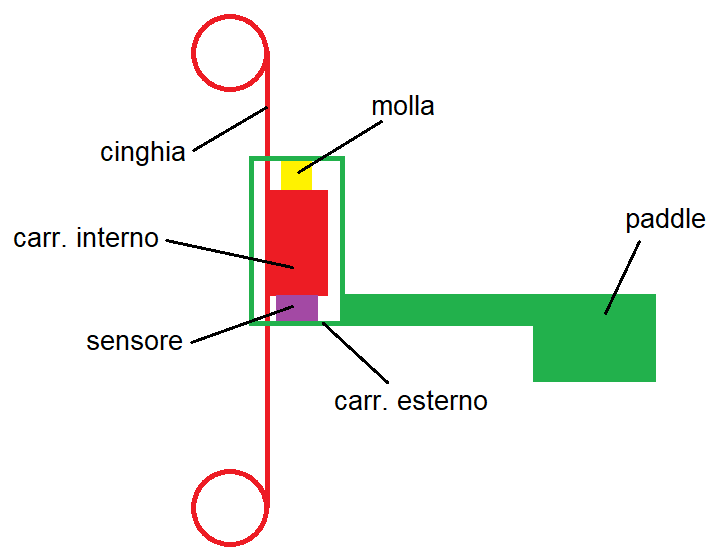
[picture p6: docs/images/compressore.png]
compressore


1. Il paddle è solidale al carrello esterno che si muove su due binari paralleli e verticali.
2. All'interno del carrello esterno, il carrello interno scorre attraverso due scanalature ricavate nel carrello esterno, in direzione parallela a quella del carrello esterno.
3. Il carrello interno è solidale alla cinghia azionata dal motore.
4. Nella parte inferiore del carrello interno è montato il sensore di pressione.
5. Nella parte superiore del carrello interno è montata una molla.
6. La molla controbilancia il peso dell'assieme verde (carrello esterno + paddle) che altrimenti, con il compressore sollevato, cadrebbe verso il basso distaccandosi dal sensore di pressione.

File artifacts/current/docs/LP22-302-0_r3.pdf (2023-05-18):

PCB/22-302-0 - Lista parti - rev. 3

Revisione | Data | Autore | Descrizione
1 | 07/12/2022 | LN | - Prima emissione.
2 | 07/03/2023 | LN | - Modificati i diodi D4, D5, D6, D7, D8, D9, D11, D13, D14, D21, D22, D23, D24, D25, D26, D27, D28 con part number SD05-01FTG, avente minor ingombro.
3 | 18/05/2023 | LN | - Inseriti i resistori R78, R79 e R80 - Inseriti i diodi D29, D30 - Inserito il jumper J9 - Modificato il connettore J8 con il part number 54548-1271 - Modificato il condensatore C37 con il valore 1uF - Modificato il regolatore U2 con il part number LD1117DT33 - Modificati gli optoisolatori U5, U7, U8, U9 con il part number TCMT1104 - Modificati i transistor Q2, Q17 con il part number BSS84

METALTRONICA S.p.a.

PCB/22-302-0 | Scheda di controllo del compressore (DiMoBIS)

Pagina 1 di 11

- Aggregato -
Pos. | Quantità | Riferimento | Valore | Descrizione | Produttore | Codice prod.
1 | 11 | C1, C2, C3, C4, C31, C33, C37, C41, C42, C44, C45 | 1u | Condensatore ceramico multistrato, 10%, 50V, SMD 0603
2 | 8 | C5, C6, C7, C8, C30, C39, C49, C50 | 10u | Condensatore ceramico multistrato, 10%, 50V, SMD 1210
3 | 2 | C9, C10 | 22p | Condensatore ceramico multistrato, 10%, 50V, SMD 0603
4 | 21 | C11, C12, C13, C14, C15, C16, C18, C22, C23, C24, C25, C26, C27, C29, C32, C40, C43, C46, C47, C48, C52 | 100n | Condensatore ceramico multistrato, 10%, 50V, SMD 0603
5 | 2 | C17, C19 | 4u7 | Condensatore ceramico multistrato, 10%, 50V, SMD 1210
6 | 2 | C20, C21 | 68p | Condensatore ceramico multistrato, 10%, 50V, SMD 0603
7 | 3 | C28, C34, C51 | 10n | Condensatore ceramico multistrato, 10%, 50V, SMD 0603
8 | 1 | C35 | 5n6 | Condensatore ceramico multistrato, 10%, 50V, SMD 0603
9 | 1 | C36 | 220n | Condensatore ceramico multistrato, 10%, 50V, SMD 0603
10 | 1 | C38 | 330u 35V | Condensatore elettrolitico alluminio, 20%, diam. 10mm, SMD
11 | 6 | DL1, DL2, DL3, DL10, DL11, DL13 | GREEN | LED verde, 20 mA, 2.2 V, SMD 0805 | Kingbright | APT2012SGC
12 | 1 | DL4 | BLUE | LED blu, 20 mA, 3,3 V, SMD 0805 | Kingbright | APT2012QBC/D
13 | 7 | DL5, DL6, DL7, DL8, DL18, DL19, DL20 | YELLOW | LED giallo, 20 mA, 2.1 V, SMD 0805 | Kingbright | APT2012YC
14 | 6 | DL9, DL12, DL14, DL15, DL16, DL17 | RED | LED rosso, 20 mA, 2 V, SMD 0805 | Kingbright | APT2012EC
15 | 5 | D1, D17, D18, D19, D20 | SMBJ30A | Diodo TVS 600W, 30V hold, 33.3V break, unidirezionale, SMD DO214AA | Littlefuse | SMBJ30A
16 | 3 | D2, D3, D29 | ES1A | Diodo rapido/ultra rapido, 50 V, 1 A, singolo, 920 mV, 15 ns, 30 A | Onsemi | ES1A
17 | 17 | D4, D5, D6, D7, D8, D9, D11, D13, D14, D21, D22, D23, D24, D25, D26, D27, D28 | SD05-01FTG | Diodo TVS 450W, 5V hold, 6V break, unidirezionale, SMD SOD323 | Littlefuse | SD05-01FTG
18 | 1 | D10 | SMBJ5.0CA | Diodo TVS 600W, 5V hold, 6.4V break, bidirezionale, SMD DO214AA | Littlefuse | SMBJ5.0CA
19 | 4 | D12, D15, D16, D30 | 1N4148WT | Diodo per piccoli segnali, 75V, 300mA, 1V, 4ns, SMD SOD-523F | Onsemi | 1N4148WT
20 | 1 | FLT1 | BNX002-11 | Filtro antirumore EMI, LC passa-basso 5° ordine, 2 canali, 10A, PTH | Murata | BNX002-11
21 | 1 | F1 | 0154005.DRT | Fusibile, azione ritardata, 5A, 125V, SMT con clip portafusibili | Littlefuse | 0154005.DRT
22 | 2 | F2, F3 | SMD050F-2 | Fusibile ripristinabile, 60V, I-hold 500mA, I-trip 1A, SMD | Littlefuse | SMD050F-2
23 | 1 | J1 | 105311-1102 | Connettore filo-scheda, serie Nano-Fit, 2 vie, passo 2.5mm, solder clip, verticale, PTH | Molex | 105311-1102
24 | 1 | J2 | HEADER-3x2 | Header maschio, 3x2 vie, passo 2.54mm, verticale, PTH | | <datasheet>
25 | 1 | J3 | 61200621621 | Connettore filo-scheda, serie WR-BHD, 3x2 vie, passo 2.54mm, verticale, PTH | Würth Elektronik | 61200621621
26 | 1 | J4 | 105310-2210 | Connettore filo-scheda, serie Nano-Fit, 5x2 vie, passo 2.5mm, verticale, PTH | Molex | 105310-2210
27 | 1 | J5 | 22-05-3031 | Connettore filo-scheda, serie KK254-7478, 3 vie, passo 2.54 mm, angolo retto, PTH | Molex | 22-05-3031
28 | 1 | J6 | MC1,5/3-G-3,81 | Morsettiera, strip maschio, 3.81mm, 3 vie, 8A, 160V, angolo retto, PTH | Phoenix Contact | MC1,5/3-G-3,81
29 | 1 | J7 | MC1,5/2-G-3,81 | Morsettiera, strip maschio, 3.81mm, 2 vie, 8A, 160V, angolo retto, PTH | Phoenix Contact | MC1,5/2-G-3,81
30 | 1 | J8 | 54548-1271 | Connettore FFC, 12 vie, passo 0.5mm, angolo retto, contatti in basso, SMD | Molex | 54548-1271
31 | 1 | J9 | HEADER-2 | Header maschio, 2 vie, passo 2.54mm, verticale, PTH
32 | 6 | L1, L2, L4, L5, L6, L7 | BLM18BD102SN1D | Perlina di ferrite, 1Kohm@100MHz, 200mA, SMD 0603 | Murata | BLM18BD102SN1D
33 | 1 | L3 | DLW32SH101XF2L | Filtro di modo comune per CAN Bus, 100uH@100kHz, 115mA, SMD 1210 | Murata | DLW32SH101XF2L

Pagina 2 di 11

- Aggregato -
Pos. | Quantità | Riferimento | Valore | Descrizione | Produttore | Codice prod.
36 | 4 | P1, P2, P3, P4 | 50k | Trimmer regolazione in testa 30 giri, 50K ohm, 10%, 0.5W | Bourns | 3296W-1-503LF
37 | 15 | Q1, Q3, Q4, Q5, Q6, Q7, Q8, Q9, Q10, Q12, Q13, Q14, Q15, Q16, Q18 | BSS138 | MOSFET canale N, 50V, 200mA, Vgs(th) 1.2V, SMD SOT-23-3 | Onsemi | BSS138
38 | 2 | Q2, Q17 | BSS84 | MOSFET canale P, -50V, -130mA, Vgs(th) -1,7V, SMD SOT-23-3 | Onsemi | BSS84
39 | 1 | Q11 | ZXMS6004FFTA | MOSFET canale N, protezioni OC OV OT, 60V, 1.3A, Vgs(th) 1.5V, SMD SOT-23-3 | Diodes Incorporated | ZXMS6004FFTA
40 | 1 | R1 | 22k | Resistore a film spesso, 1%, 1/10W, SMD 0603
41 | 4 | R2, R9, R10, R30 | 2k | Resistore a film spesso, 1%, 1/10W, SMD 0603
42 | 1 | R3 | 2k2 | Resistore a film spesso, 1%, 1/4W, SMD 1206
43 | 4 | R4, R20, R42, R47 | 330 | Resistore a film spesso, 1%, 1/10W, SMD 0603
44 | 10 | R5, R39, R40, R55, R56, R59, R62, R71, R72, R73 | 120 Resistore a film spesso, 1%, 1/10W, SMD 0603
45 | 1 | R6 | JUMPER | Resistore a film spesso, 1%, 1/8W, SMD 0805
46 | 20 | R7, R14, R33, R35, R44, R45, R46, R48, R49, R50, R65, R66, R67, R68, R74, R75, R76, R77, R78, R80 | 10k | Resistore a film spesso, 1%, 1/10W, SMD 0603
47 | 11 | R8, R16, R18, R51, R52, R57, R60, R63, R64, R69, R70 | 1k | Resistore a film spesso, 1%, 1/10W, SMD 0603
48 | 1 | R11 | 220 | Resistore a film spesso, 1%, 1/10W, SMD 0603
49 | 1 | R12 | 4k | Resistore a film spesso, 1%, 1/10W, SMD 0603
50 | 1 | R13 | 0 | Resistore a film spesso, 1%, 1/10W, SMD 0603
51 | 1 | R15 | 560 | Resistore a film spesso, 1%, 1/10W, SMD 0603
52 | 4 | R17, R21, R23, R25 | 680 | Resistore a film spesso, 1%, 1/10W, SMD 0603
53 | 4 | R19, R22, R24, R26 | 270 | Resistore a film spesso, 1%, 1/10W, SMD 0603
54 | 5 | R27, R53, R54, R58, R61 | 10 | Resistore a film spesso, 1%, 1/10W, SMD 0603
55 | 1 | R28 | 18k | Resistore a film spesso, 1%, 1/10W, SMD 0603
56 | 2 | R29, R38 | 100 | Resistore a film spesso, 1%, 1/10W, SMD 0603
57 | 4 | R31, R32, R34, R36 | 20k | Resistore a film spesso, 1%, 1/10W, SMD 0603
58 | 2 | R37, R79 | 100k | Resistore a film spesso, 1%, 1/10W, SMD 0603
59 | 1 | R41 | 0R1 - 2W | Resistore a film spesso, 1%, 2W, SMD 2512
60 | 1 | R43 | 150 | Resistore a film spesso, 1%, 1/10W, SMD 0603
62 | 1 | U1 | R-78E5.0-1.0 | Regolatore di tensione switching, 8V-28V in, 5V out, 1A, PTH | Recom | R-78E5.0-1.0
63 | 1 | U2 | LD1117DT33 | Regolatore di tensione lineare fisso, LDO, 3.5V-20V in, 3.3V out, 1A, SMD DPAK | ST | LD1117DT33TR
64 | 1 | U3 | ATSAME51J20A-AU | 32-bit ARM Cortex-M4F, 1MB Flash, 256kB RAM, 2xCAN-FD, 1.7V to 3.6V, TQFP64, Industrial temp | Microchip | ATSAME51J20A-AU
65 | 1 | U4 | TJA1050T | High speed CAN tranceiver, 1TX/1RX, 5V, SMD SOIC8 | NXP | TJA1050T/CM,118
66 | 4 | U5, U7, U8, U9 | TCMT1104 | Optoisolatore singolo, CTR 160%-320%, SMD 4-SOP | Clare | TCMT1104
67 | 1 | U6 | CPC1017N | Relè a stato solido, 60V, 100mA, SMD 4-SOP | IXYS | CPC1017N
68 | 2 | U10, U15 | MCP6004-I/ST | Amplificatore operazionale, quadruplo, 1 MHz, 0.6 V/µs, 1.8V-6V, SMD TSSOP-14 | Microchip | MCP6004-I/ST
69 | 1 | U11 | L6205PD | Driver/controllore motore, ponte intero, alim 8V-52V, 52V/2.8A/4 output, SMD PowerSO20 | ST | L6205PD
70 | 1 | U12 | CPC1916Y | Relè a stato solido, 100V, 2.5A, PTH SIP | IXYS | CPC1916Y
71 | 2 | U13, U14 | MCP4661-503E/ST | Potenziometro digitale, doppio, non volatile, 50kohm, 8 bit, I2C, SMD TSSOP-14 | Microchip | MCP4661-503E/ST

Pagina 3 di 11

- Aggregato -
Pos. | Quantità | Riferimento | Valore | Descrizione | Produttore | Codice prod.
72 | 1 | U16 | MCP6002-I/MS | Amplificatore operazionale, doppio, 1 MHz, 0.6 V/µs, 1.8V-6V, SMD MSOP-8 | Microchip | MCP6002-I/MS
73 | 1 | U17 | SN74HCS365PWR | Buffer e line driver, 6 porte, trigger di Schmitt, SMD TSSOP-16 | Texas Instruments | SN74HCS365PWR
74 | 1 | XT1 | 32.768kHz | Quarzo 32.768kHz, 20ppm, 12.5pF, SMD 1.6mmx1mm | ECS | ECS-.327-12.5-16-TR3

Pagina 4 di 11

- Esploso -
C1 | 1u | Condensatore ceramico multistrato, 10%, 50V, SMD 0603
C2 | 1u | Condensatore ceramico multistrato, 10%, 50V, SMD 0603
C3 | 1u | Condensatore ceramico multistrato, 10%, 50V, SMD 0603
C4 | 1u | Condensatore ceramico multistrato, 10%, 50V, SMD 0603
C5 | 10u | Condensatore ceramico multistrato, 10%, 50V, SMD 1210
C6 | 10u | Condensatore ceramico multistrato, 10%, 50V, SMD 1210
C7 | 10u | Condensatore ceramico multistrato, 10%, 50V, SMD 1210
C8 | 10u | Condensatore ceramico multistrato, 10%, 50V, SMD 1210
C9 | 22p | Condensatore ceramico multistrato, 10%, 50V, SMD 0603
C10 | 22p | Condensatore ceramico multistrato, 10%, 50V, SMD 0603
C11 | 100n | Condensatore ceramico multistrato, 10%, 50V, SMD 0603
C12 | 100n | Condensatore ceramico multistrato, 10%, 50V, SMD 0603
C13 | 100n | Condensatore ceramico multistrato, 10%, 50V, SMD 0603
C14 | 100n | Condensatore ceramico multistrato, 10%, 50V, SMD 0603
C15 | 100n | Condensatore ceramico multistrato, 10%, 50V, SMD 0603
C16 | 100n | Condensatore ceramico multistrato, 10%, 50V, SMD 0603
C17 | 4u7 | Condensatore ceramico multistrato, 10%, 50V, SMD 1210
C18 | 100n | Condensatore ceramico multistrato, 10%, 50V, SMD 0603
C19 | 4u7 | Condensatore ceramico multistrato, 10%, 50V, SMD 1210
C20 | 68p | Condensatore ceramico multistrato, 10%, 50V, SMD 0603
C21 | 68p | Condensatore ceramico multistrato, 10%, 50V, SMD 0603
C22 | 100n | Condensatore ceramico multistrato, 10%, 50V, SMD 0603
C23 | 100n | Condensatore ceramico multistrato, 10%, 50V, SMD 0603
C24 | 100n | Condensatore ceramico multistrato, 10%, 50V, SMD 0603
C25 | 100n | Condensatore ceramico multistrato, 10%, 50V, SMD 0603
C26 | 100n | Condensatore ceramico multistrato, 10%, 50V, SMD 0603
C27 | 100n | Condensatore ceramico multistrato, 10%, 50V, SMD 0603
C28 | 10n | Condensatore ceramico multistrato, 10%, 50V, SMD 0603
C29 | 100n | Condensatore ceramico multistrato, 10%, 50V, SMD 0603
C30 | 10u | Condensatore ceramico multistrato, 10%, 50V, SMD 1210
C31 | 1u | Condensatore ceramico multistrato, 10%, 50V, SMD 0603
C32 | 100n | Condensatore ceramico multistrato, 10%, 50V, SMD 0603
C33 | 1u | Condensatore ceramico multistrato, 10%, 50V, SMD 0603
C34 | 10n | Condensatore ceramico multistrato, 10%, 50V, SMD 0603
C35 | 5n6 | Condensatore ceramico multistrato, 10%, 50V, SMD 0603
C36 | 220n | Condensatore ceramico multistrato, 10%, 50V, SMD 0603
C37 | 1u | Condensatore ceramico multistrato, 10%, 50V, SMD 0603
C38 | 330u 35V | Condensatore elettrolitico alluminio, 20%, diam. 10mm, SMD
C39 | 10u | Condensatore ceramico multistrato, 10%, 50V, SMD 1210
C40 | 100n | Condensatore ceramico multistrato, 10%, 50V, SMD 0603
C41 | 1u | Condensatore ceramico multistrato, 10%, 50V, SMD 0603
C42 | 1u | Condensatore ceramico multistrato, 10%, 50V, SMD 0603
Riferimento | Valore | Descrizione | Produttore | Codice Prod | ASSY-00
Montare | Note

Pagina 5 di 11

Riferimento | Valore | Descrizione | Produttore | Codice Prod | ASSY-00
Montare | Note
C43 | 100n | Condensatore ceramico multistrato, 10%, 50V, SMD 0603
C44 | 1u | Condensatore ceramico multistrato, 10%, 50V, SMD 0603
C45 | 1u | Condensatore ceramico multistrato, 10%, 50V, SMD 0603
C46 | 100n | Condensatore ceramico multistrato, 10%, 50V, SMD 0603
C47 | 100n | Condensatore ceramico multistrato, 10%, 50V, SMD 0603
C48 | 100n | Condensatore ceramico multistrato, 10%, 50V, SMD 0603
C49 | 10u | Condensatore ceramico multistrato, 10%, 50V, SMD 1210
C50 | 10u | Condensatore ceramico multistrato, 10%, 50V, SMD 1210
C51 | 10n | Condensatore ceramico multistrato, 10%, 50V, SMD 0603
C52 | 100n | Condensatore ceramico multistrato, 10%, 50V, SMD 0603
D1 | SMBJ30A | Diodo TVS 600W, 30V hold, 33.3V break, unidirezionale, SMD DO214AA | Littlefuse | SMBJ30A
D2 | ES1A | Diodo rapido/ultra rapido, 50 V, 1 A, singolo, 920 mV, 15 ns, 30 A | Onsemi | ES1A
D3 | ES1A | Diodo rapido/ultra rapido, 50 V, 1 A, singolo, 920 mV, 15 ns, 30 A | Onsemi | ES1A
D4 | SD05-01FTG | Diodo TVS 450W, 5V hold, 6V break, unidirezionale, SMD SOD323 | Littlefuse | SD05-01FTG
D5 | SD05-01FTG | Diodo TVS 450W, 5V hold, 6V break, unidirezionale, SMD SOD323 | Littlefuse | SD05-01FTG
D6 | SD05-01FTG | Diodo TVS 450W, 5V hold, 6V break, unidirezionale, SMD SOD323 | Littlefuse | SD05-01FTG
D7 | SD05-01FTG | Diodo TVS 450W, 5V hold, 6V break, unidirezionale, SMD SOD323 | Littlefuse | SD05-01FTG
D8 | SD05-01FTG | Diodo TVS 450W, 5V hold, 6V break, unidirezionale, SMD SOD323 | Littlefuse | SD05-01FTG
D9 | SD05-01FTG | Diodo TVS 450W, 5V hold, 6V break, unidirezionale, SMD SOD323 | Littlefuse | SD05-01FTG
D10 | SMBJ5.0CA | Diodo TVS 600W, 5V hold, 6.4V break, bidirezionale, SMD DO214AA | Littlefuse | SMBJ5.0CA
D11 | SD05-01FTG | Diodo TVS 450W, 5V hold, 6V break, unidirezionale, SMD SOD323 | Littlefuse | SD05-01FTG
D12 | 1N4148WT | Diodo per piccoli segnali, 75V, 300mA, 1V, 4ns, SMD SOD-523F | Onsemi | 1N4148WT
D13 | SD05-01FTG | Diodo TVS 450W, 5V hold, 6V break, unidirezionale, SMD SOD323 | Littlefuse | SD05-01FTG
D14 | SD05-01FTG | Diodo TVS 450W, 5V hold, 6V break, unidirezionale, SMD SOD323 | Littlefuse | SD05-01FTG
D15 | 1N4148WT | Diodo per piccoli segnali, 75V, 300mA, 1V, 4ns, SMD SOD-523F | Onsemi | 1N4148WT
D16 | 1N4148WT | Diodo per piccoli segnali, 75V, 300mA, 1V, 4ns, SMD SOD-523F | Onsemi | 1N4148WT
D17 | SMBJ30A | Diodo TVS 600W, 30V hold, 33.3V break, unidirezionale, SMD DO214AA | Littlefuse | SMBJ30A
D18 | SMBJ30A | Diodo TVS 600W, 30V hold, 33.3V break, unidirezionale, SMD DO214AA | Littlefuse | SMBJ30A
D19 | SMBJ30A | Diodo TVS 600W, 30V hold, 33.3V break, unidirezionale, SMD DO214AA | Littlefuse | SMBJ30A
D20 | SMBJ30A | Diodo TVS 600W, 30V hold, 33.3V break, unidirezionale, SMD DO214AA | Littlefuse | SMBJ30A
D21 | SD05-01FTG | Diodo TVS 450W, 5V hold, 6V break, unidirezionale, SMD SOD323 | Littlefuse | SD05-01FTG
D22 | SD05-01FTG | Diodo TVS 450W, 5V hold, 6V break, unidirezionale, SMD SOD323 | Littlefuse | SD05-01FTG
D23 | SD05-01FTG | Diodo TVS 450W, 5V hold, 6V break, unidirezionale, SMD SOD323 | Littlefuse | SD05-01FTG
D24 | SD05-01FTG | Diodo TVS 450W, 5V hold, 6V break, unidirezionale, SMD SOD323 | Littlefuse | SD05-01FTG
D25 | SD05-01FTG | Diodo TVS 450W, 5V hold, 6V break, unidirezionale, SMD SOD323 | Littlefuse | SD05-01FTG
D26 | SD05-01FTG | Diodo TVS 450W, 5V hold, 6V break, unidirezionale, SMD SOD323 | Littlefuse | SD05-01FTG
D27 | SD05-01FTG | Diodo TVS 450W, 5V hold, 6V break, unidirezionale, SMD SOD323 | Littlefuse | SD05-01FTG
D28 | SD05-01FTG | Diodo TVS 450W, 5V hold, 6V break, unidirezionale, SMD SOD323 | Littlefuse | SD05-01FTG
D29 | ES1A | Diodo rapido/ultra rapido, 50 V, 1 A, singolo, 920 mV, 15 ns, 30 A | Onsemi | ES1A
D30 | 1N4148WT | Diodo per piccoli segnali, 75V, 300mA, 1V, 4ns, SMD SOD-523F | Onsemi | 1N4148WT
DL1 | GREEN | LED verde, 20 mA, 2.2 V, SMD 0805 | Kingbright | APT2012SGC
DL2 | GREEN | LED verde, 20 mA, 2.2 V, SMD 0805 | Kingbright | APT2012SGC

Pagina 6 di 11

Riferimento | Valore | Descrizione | Produttore | Codice Prod | ASSY-00
Montare | Note
DL3 | GREEN | LED verde, 20 mA, 2.2 V, SMD 0805 | Kingbright | APT2012SGC
DL4 | BLUE | LED blu, 20 mA, 3,3 V, SMD 0805 | Kingbright | APT2012QBC/D
DL5 | YELLOW | LED giallo, 20 mA, 2.1 V, SMD 0805 | Kingbright | APT2012YC
DL6 | YELLOW | LED giallo, 20 mA, 2.1 V, SMD 0805 | Kingbright | APT2012YC
DL7 | YELLOW | LED giallo, 20 mA, 2.1 V, SMD 0805 | Kingbright | APT2012YC
DL8 | YELLOW | LED giallo, 20 mA, 2.1 V, SMD 0805 | Kingbright | APT2012YC
DL9 | RED | LED rosso, 20 mA, 2 V, SMD 0805 | Kingbright | APT2012EC
DL10 | GREEN | LED verde, 20 mA, 2.2 V, SMD 0805 | Kingbright | APT2012SGC
DL11 | GREEN | LED verde, 20 mA, 2.2 V, SMD 0805 | Kingbright | APT2012SGC
DL12 | RED | LED rosso, 20 mA, 2 V, SMD 0805 | Kingbright | APT2012EC
DL13 | GREEN | LED verde, 20 mA, 2.2 V, SMD 0805 | Kingbright | APT2012SGC
DL14 | RED | LED rosso, 20 mA, 2 V, SMD 0805 | Kingbright | APT2012EC
DL15 | RED | LED rosso, 20 mA, 2 V, SMD 0805 | Kingbright | APT2012EC
DL16 | RED | LED rosso, 20 mA, 2 V, SMD 0805 | Kingbright | APT2012EC
DL17 | RED | LED rosso, 20 mA, 2 V, SMD 0805 | Kingbright | APT2012EC
DL18 | YELLOW | LED giallo, 20 mA, 2.1 V, SMD 0805 | Kingbright | APT2012YC
DL19 | YELLOW | LED giallo, 20 mA, 2.1 V, SMD 0805 | Kingbright | APT2012YC
DL20 | YELLOW | LED giallo, 20 mA, 2.1 V, SMD 0805 | Kingbright | APT2012YC
F1 | 0154005.DRT | Fusibile, azione ritardata, 5A, 125V, SMT con clip portafusibili | Littlefuse | 0154005.DRT
F2 | SMD050F-2 | Fusibile ripristinabile, 60V, I-hold 500mA, I-trip 1A, SMD | Littlefuse | SMD050F-2
F3 | SMD050F-2 | Fusibile ripristinabile, 60V, I-hold 500mA, I-trip 1A, SMD | Littlefuse | SMD050F-2
FLT1 | BNX002-11 | Filtro antirumore EMI, LC passa-basso 5° ordine, 2 canali, 10A, PTH | Murata | BNX002-11
J1 | 105311-1102 | Connettore filo-scheda, serie Nano-Fit, 2 vie, passo 2.5mm, solder clip, verticale, PTH | Molex | 105311-1102
J2 | HEADER-3x2 | Header maschio, 3x2 vie, passo 2.54mm, verticale, PTH
J3 | 61200621621 | Connettore filo-scheda, serie WR-BHD, 3x2 vie, passo 2.54mm, verticale, PTH | Würth Elektronik | 61200621621
J4 | 105310-2210 | Connettore filo-scheda, serie Nano-Fit, 5x2 vie, passo 2.5mm, verticale, PTH | Molex | 105310-2210
J5 | 22-05-3031 | Connettore filo-scheda, serie KK254-7478, 3 vie, passo 2.54 mm, angolo retto, PTH | Molex | 22-05-3031
J6 | MC1,5/3-G-3,81 | Morsettiera, strip maschio, 3.81mm, 3 vie, 8A, 160V, angolo retto, PTH | Phoenix Contact | MC1,5/3-G-3,81
J7 | MC1,5/2-G-3,81 | Morsettiera, strip maschio, 3.81mm, 2 vie, 8A, 160V, angolo retto, PTH | Phoenix Contact | MC1,5/2-G-3,81
J8 | 54548-1271 | Connettore FFC, 12 vie, passo 0.5mm, angolo retto, contatti in basso, SMD | Molex | 54548-1271
J9 | HEADER-2 | Header maschio, 2 vie, passo 2.54mm, verticale, PTH
L1 | BLM18BD102SN1D | Perlina di ferrite, 1Kohm@100MHz, 200mA, SMD 0603 | Murata | BLM18BD102SN1D
L2 | BLM18BD102SN1D | Perlina di ferrite, 1Kohm@100MHz, 200mA, SMD 0603 | Murata | BLM18BD102SN1D
L3 | DLW32SH101XF2L | Filtro di modo comune per CAN Bus, 100uH@100kHz, 115mA, SMD 1210 | Murata | DLW32SH101XF2L
L4 | BLM18BD102SN1D | Perlina di ferrite, 1Kohm@100MHz, 200mA, SMD 0603 | Murata | BLM18BD102SN1D
L5 | BLM18BD102SN1D | Perlina di ferrite, 1Kohm@100MHz, 200mA, SMD 0603 | Murata | BLM18BD102SN1D
L6 | BLM18BD102SN1D | Perlina di ferrite, 1Kohm@100MHz, 200mA, SMD 0603 | Murata | BLM18BD102SN1D
L7 | BLM18BD102SN1D | Perlina di ferrite, 1Kohm@100MHz, 200mA, SMD 0603 | Murata | BLM18BD102SN1D
P1 | 50k | Trimmer regolazione in testa 30 giri, 50K ohm, 10%, 0.5W | Bourns | 3296W-1-503LF | NO
P2 | 50k | Trimmer regolazione in testa 30 giri, 50K ohm, 10%, 0.5W | Bourns | 3296W-1-503LF | NO
P3 | 50k | Trimmer regolazione in testa 30 giri, 50K ohm, 10%, 0.5W | Bourns | 3296W-1-503LF | NO
P4 | 50k | Trimmer regolazione in testa 30 giri, 50K ohm, 10%, 0.5W | Bourns | 3296W-1-503LF | NO

Pagina 7 di 11

Riferimento | Valore | Descrizione | Produttore | Codice Prod | ASSY-00
Montare | Note
Q1 | BSS138 | MOSFET canale N, 50V, 200mA, Vgs(th) 1.2V, SMD SOT-23-3 | Onsemi | BSS138
Q2 | BSS84 | MOSFET canale P, -50V, -130mA, Vgs(th) -1,7V, SMD SOT-23-3 | Onsemi | BSS84
Q3 | BSS138 | MOSFET canale N, 50V, 200mA, Vgs(th) 1.2V, SMD SOT-23-3 | Onsemi | BSS138
Q4 | BSS138 | MOSFET canale N, 50V, 200mA, Vgs(th) 1.2V, SMD SOT-23-3 | Onsemi | BSS138
Q5 | BSS138 | MOSFET canale N, 50V, 200mA, Vgs(th) 1.2V, SMD SOT-23-3 | Onsemi | BSS138
Q6 | BSS138 | MOSFET canale N, 50V, 200mA, Vgs(th) 1.2V, SMD SOT-23-3 | Onsemi | BSS138
Q7 | BSS138 | MOSFET canale N, 50V, 200mA, Vgs(th) 1.2V, SMD SOT-23-3 | Onsemi | BSS138
Q8 | BSS138 | MOSFET canale N, 50V, 200mA, Vgs(th) 1.2V, SMD SOT-23-3 | Onsemi | BSS138
Q9 | BSS138 | MOSFET canale N, 50V, 200mA, Vgs(th) 1.2V, SMD SOT-23-3 | Onsemi | BSS138
Q10 | BSS138 | MOSFET canale N, 50V, 200mA, Vgs(th) 1.2V, SMD SOT-23-3 | Onsemi | BSS138
Q11 | ZXMS6004FFTA | MOSFET canale N, protezioni OC OV OT, 60V, 1.3A, Vgs(th) 1.5V, SMD SOT-23-3 | Diodes Incorporated | ZXMS6004FFTA
Q12 | BSS138 | MOSFET canale N, 50V, 200mA, Vgs(th) 1.2V, SMD SOT-23-3 | Onsemi | BSS138
Q13 | BSS138 | MOSFET canale N, 50V, 200mA, Vgs(th) 1.2V, SMD SOT-23-3 | Onsemi | BSS138
Q14 | BSS138 | MOSFET canale N, 50V, 200mA, Vgs(th) 1.2V, SMD SOT-23-3 | Onsemi | BSS138
Q15 | BSS138 | MOSFET canale N, 50V, 200mA, Vgs(th) 1.2V, SMD SOT-23-3 | Onsemi | BSS138
Q16 | BSS138 | MOSFET canale N, 50V, 200mA, Vgs(th) 1.2V, SMD SOT-23-3 | Onsemi | BSS138
Q17 | BSS84 | MOSFET canale P, -50V, -130mA, Vgs(th) -1,7V, SMD SOT-23-3 | Onsemi | BSS84
Q18 | BSS138 | MOSFET canale N, 50V, 200mA, Vgs(th) 1.2V, SMD SOT-23-3 | Onsemi | BSS138
R1 | 22k | Resistore a film spesso, 1%, 1/10W, SMD 0603
R2 | 2k | Resistore a film spesso, 1%, 1/10W, SMD 0603
R3 | 2k2 | Resistore a film spesso, 1%, 1/4W, SMD 1206
R4 | 330 | Resistore a film spesso, 1%, 1/10W, SMD 0603
R5 | 120 | Resistore a film spesso, 1%, 1/10W, SMD 0603
R6 | JUMPER | Resistore a film spesso, 1%, 1/8W, SMD 0805
R7 | 10k | Resistore a film spesso, 1%, 1/10W, SMD 0603
R8 | 1k | Resistore a film spesso, 1%, 1/10W, SMD 0603
R9 | 2k | Resistore a film spesso, 1%, 1/10W, SMD 0603
R10 | 2k | Resistore a film spesso, 1%, 1/10W, SMD 0603
R11 | 220 | Resistore a film spesso, 1%, 1/10W, SMD 0603
R12 | 4k | Resistore a film spesso, 1%, 1/10W, SMD 0603
R13 | 0 | Resistore a film spesso, 1%, 1/10W, SMD 0603
R14 | 10k | Resistore a film spesso, 1%, 1/10W, SMD 0603
R15 | 560 | Resistore a film spesso, 1%, 1/10W, SMD 0603
R16 | 1k | Resistore a film spesso, 1%, 1/10W, SMD 0603
R17 | 680 | Resistore a film spesso, 1%, 1/10W, SMD 0603
R18 | 1k | Resistore a film spesso, 1%, 1/10W, SMD 0603
R19 | 270 | Resistore a film spesso, 1%, 1/10W, SMD 0603
R20 | 330 | Resistore a film spesso, 1%, 1/10W, SMD 0603
R21 | 680 | Resistore a film spesso, 1%, 1/10W, SMD 0603
R22 | 270 | Resistore a film spesso, 1%, 1/10W, SMD 0603
R23 | 680 | Resistore a film spesso, 1%, 1/10W, SMD 0603
R24 | 270 | Resistore a film spesso, 1%, 1/10W, SMD 0603

Pagina 8 di 11

Riferimento | Valore | Descrizione | Produttore | Codice Prod | ASSY-00
Montare | Note
R25 | 680 | Resistore a film spesso, 1%, 1/10W, SMD 0603
R26 | 270 | Resistore a film spesso, 1%, 1/10W, SMD 0603
R27 | 10 | Resistore a film spesso, 1%, 1/10W, SMD 0603
R28 | 18k | Resistore a film spesso, 1%, 1/10W, SMD 0603
R29 | 100 | Resistore a film spesso, 1%, 1/10W, SMD 0603
R30 | 2k | Resistore a film spesso, 1%, 1/10W, SMD 0603
R31 | 20k | Resistore a film spesso, 1%, 1/10W, SMD 0603
R32 | 20k | Resistore a film spesso, 1%, 1/10W, SMD 0603
R33 | 10k | Resistore a film spesso, 1%, 1/10W, SMD 0603
R34 | 20k | Resistore a film spesso, 1%, 1/10W, SMD 0603
R35 | 10k | Resistore a film spesso, 1%, 1/10W, SMD 0603
R36 | 20k | Resistore a film spesso, 1%, 1/10W, SMD 0603
R37 | 100k | Resistore a film spesso, 1%, 1/10W, SMD 0603
R38 | 100 | Resistore a film spesso, 1%, 1/10W, SMD 0603
R39 | 120 | Resistore a film spesso, 1%, 1/10W, SMD 0603
R40 | 120 | Resistore a film spesso, 1%, 1/10W, SMD 0603
R41 | 0R1 - 2W | Resistore a film spesso, 1%, 2W, SMD 2512
R42 | 330 | Resistore a film spesso, 1%, 1/10W, SMD 0603
R43 | 150 | Resistore a film spesso, 1%, 1/10W, SMD 0603
R44 | 10k | Resistore a film spesso, 1%, 1/10W, SMD 0603
R45 | 10k | Resistore a film spesso, 1%, 1/10W, SMD 0603
R46 | 10k | Resistore a film spesso, 1%, 1/10W, SMD 0603
R47 | 330 | Resistore a film spesso, 1%, 1/10W, SMD 0603
R48 | 10k | Resistore a film spesso, 1%, 1/10W, SMD 0603
R49 | 10k | Resistore a film spesso, 1%, 1/10W, SMD 0603
R50 | 10k | Resistore a film spesso, 1%, 1/10W, SMD 0603
R51 | 1k | Resistore a film spesso, 1%, 1/10W, SMD 0603
R52 | 1k | Resistore a film spesso, 1%, 1/10W, SMD 0603
R53 | 10 | Resistore a film spesso, 1%, 1/10W, SMD 0603
R54 | 10 | Resistore a film spesso, 1%, 1/10W, SMD 0603
R55 | 120 | Resistore a film spesso, 1%, 1/10W, SMD 0603
R56 | 120 | Resistore a film spesso, 1%, 1/10W, SMD 0603
R57 | 1k | Resistore a film spesso, 1%, 1/10W, SMD 0603
R58 | 10 | Resistore a film spesso, 1%, 1/10W, SMD 0603
R59 | 120 | Resistore a film spesso, 1%, 1/10W, SMD 0603
R60 | 1k | Resistore a film spesso, 1%, 1/10W, SMD 0603
R61 | 10 | Resistore a film spesso, 1%, 1/10W, SMD 0603
R62 | 120 | Resistore a film spesso, 1%, 1/10W, SMD 0603
R63 | 1k | Resistore a film spesso, 1%, 1/10W, SMD 0603
R64 | 1k | Resistore a film spesso, 1%, 1/10W, SMD 0603
R65 | 10k | Resistore a film spesso, 1%, 1/10W, SMD 0603
R66 | 10k | Resistore a film spesso, 1%, 1/10W, SMD 0603

Pagina 9 di 11

Riferimento | Valore | Descrizione | Produttore | Codice Prod | ASSY-00
Montare | Note
R67 | 10k | Resistore a film spesso, 1%, 1/10W, SMD 0603
R68 | 10k | Resistore a film spesso, 1%, 1/10W, SMD 0603
R69 | 1k | Resistore a film spesso, 1%, 1/10W, SMD 0603
R70 | 1k | Resistore a film spesso, 1%, 1/10W, SMD 0603
R71 | 120 | Resistore a film spesso, 1%, 1/10W, SMD 0603
R72 | 120 | Resistore a film spesso, 1%, 1/10W, SMD 0603
R73 | 120 | Resistore a film spesso, 1%, 1/10W, SMD 0603
R74 | 10k | Resistore a film spesso, 1%, 1/10W, SMD 0603
R75 | 10k | Resistore a film spesso, 1%, 1/10W, SMD 0603
R76 | 10k | Resistore a film spesso, 1%, 1/10W, SMD 0603
R77 | 10k | Resistore a film spesso, 1%, 1/10W, SMD 0603
R78 | 10k | Resistore a film spesso, 1%, 1/10W, SMD 0603
R79 | 100k | Resistore a film spesso, 1%, 1/10W, SMD 0603
R80 | 10k | Resistore a film spesso, 1%, 1/10W, SMD 0603
U1 | R-78E5.0-1.0 | Regolatore di tensione switching, 8V-28V in, 5V out, 1A, PTH | Recom | R-78E5.0-1.0
U2 | LD1117DT33 | Regolatore di tensione lineare fisso, LDO, 3.5V-20V in, 3.3V out, 1A, SMD DPAK | ST | LD1117DT33TR
U3 | ATSAME51J20A-AU | 32-bit ARM Cortex-M4F, 1MB Flash, 256kB RAM, 2xCAN-FD, 1.7V to 3.6V, TQFP64, Industrial temp | Microchip | ATSAME51J20A-AU
U4 | TJA1050T | High speed CAN tranceiver, 1TX/1RX, 5V, SMD SOIC8 | NXP | TJA1050T/CM,118
U5 | TCMT1104 | Optoisolatore singolo, CTR 160%-320%, SMD 4-SOP | Clare | TCMT1104
U6 | CPC1017N | Relè a stato solido, 60V, 100mA, SMD 4-SOP | IXYS | CPC1017N
U7 | TCMT1104 | Optoisolatore singolo, CTR 160%-320%, SMD 4-SOP | Clare | TCMT1104
U8 | TCMT1104 | Optoisolatore singolo, CTR 160%-320%, SMD 4-SOP | Clare | TCMT1104
U9 | TCMT1104 | Optoisolatore singolo, CTR 160%-320%, SMD 4-SOP | Clare | TCMT1104
U10 | MCP6004-I/ST | Amplificatore operazionale, quadruplo, 1 MHz, 0.6 V/µs, 1.8V-6V, SMD TSSOP-14 | Microchip | MCP6004-I/ST
U11 | L6205PD | Driver/controllore motore, ponte intero, alim 8V-52V, 52V/2.8A/4 output, SMD PowerSO20 | ST | L6205PD
U12 | CPC1916Y | Relè a stato solido, 100V, 2.5A, PTH SIP | IXYS | CPC1916Y
U13 | MCP4661-503E/ST | Potenziometro digitale, doppio, non volatile, 50kohm, 8 bit, I2C, SMD TSSOP-14 | Microchip | MCP4661-503E/ST
U14 | MCP4661-503E/ST | Potenziometro digitale, doppio, non volatile, 50kohm, 8 bit, I2C, SMD TSSOP-14 | Microchip | MCP4661-503E/ST
U15 | MCP6004-I/ST | Amplificatore operazionale, quadruplo, 1 MHz, 0.6 V/µs, 1.8V-6V, SMD TSSOP-14 | Microchip | MCP6004-I/ST
U16 | MCP6002-I/MS | Amplificatore operazionale, doppio, 1 MHz, 0.6 V/µs, 1.8V-6V, SMD MSOP-8 | Microchip | MCP6002-I/MS
U17 | SN74HCS365PWR | Buffer e line driver, 6 porte, trigger di Schmitt, SMD TSSOP-16 | Texas Instruments | SN74HCS365PWR
XT1 | 32.768kHz | Quarzo 32.768kHz, 20ppm, 12.5pF, SMD 1.6mmx1mm | ECS | ECS-.327-12.5-16-TR3

Pagina 10 di 11

## Nota 1 Circuito stampato CS/22-302-0 - materiale : FR4 - spessore scheda : 1.6mm - strati : 4 - spessore rame : 35um

## Pagina 11 di 11

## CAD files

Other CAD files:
artifacts/current/layout/drawings/22-302-0.dwg
artifacts/current/layout/drawings/PM22-302-0.dwg
artifacts/current/layout/drawings/PF22-302-0.dwg

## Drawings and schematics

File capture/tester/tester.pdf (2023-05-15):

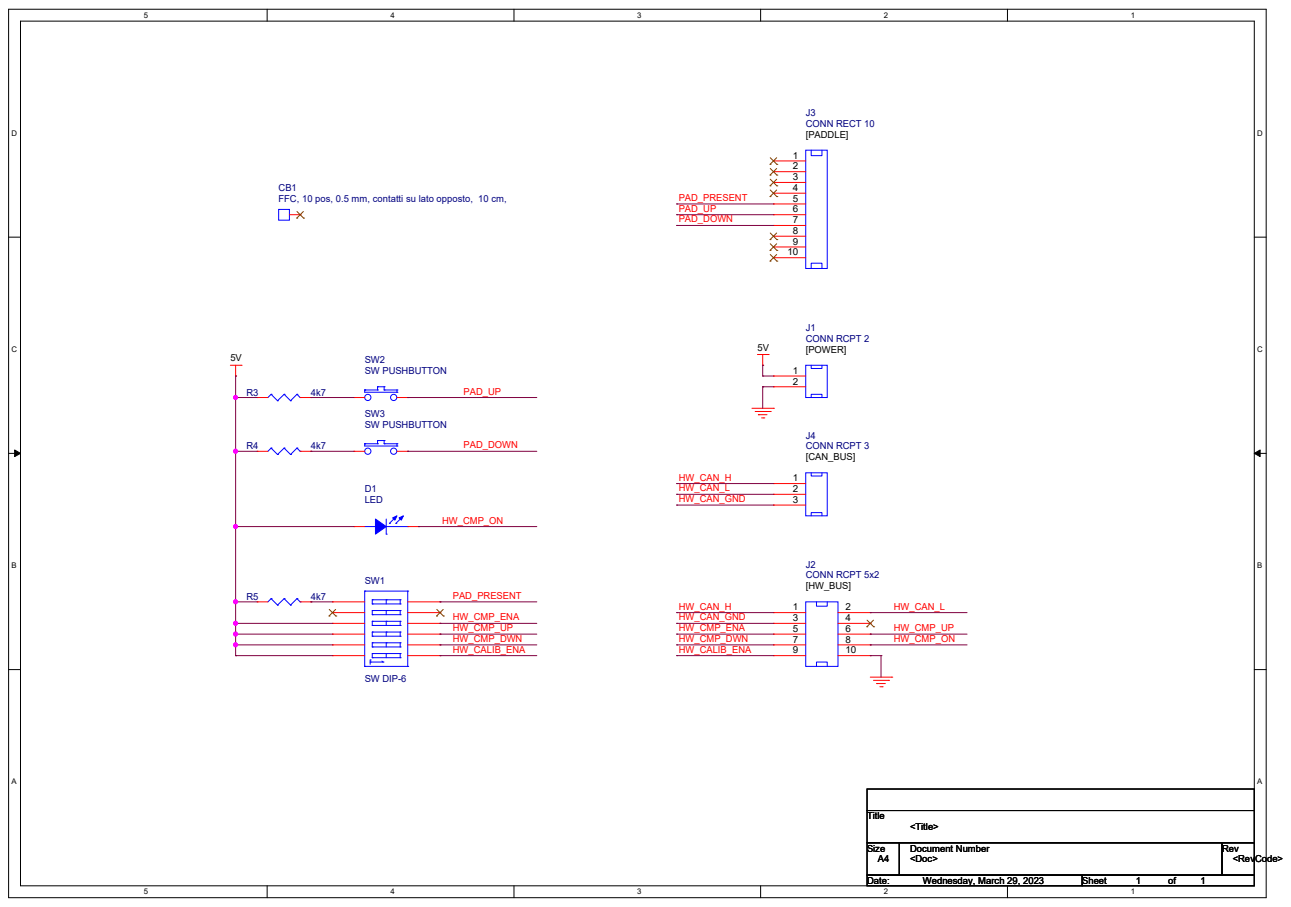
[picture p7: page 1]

FFC, 10 pos, 0.5 mm, contatti su lato opposto, 10 cm,

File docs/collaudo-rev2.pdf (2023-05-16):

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
METALTRONICA S.p.a.

# PCB/22-302-0 Scheda di controllo del compressore (DiMoBIS)

Revisione | Data | Autore | Descrizione
1 | 07/12/2022 | LN | Prima emissione
| | | Sostituiti i diodi D4, D5, D6, D7, D8, D9, D11, D13, D14, D21, D22, D23, D24, D25, D26, D27, D28 con il part number SD05-01FTG.
2 | 07/03/2023 | LN

Title

Size | Document Number | Rev
Date: | Sheet | of
| PCB/22-302-0 | 2

REVISIONS

A4 | Tuesday, March 07, 2023 | 1 | 12 Title
REVISIONS
A4 | Tuesday, March 07, 2023 | 1 | 12 Title
REVISIONS
A4 | Tuesday, March 07, 2023 | 1 | 12

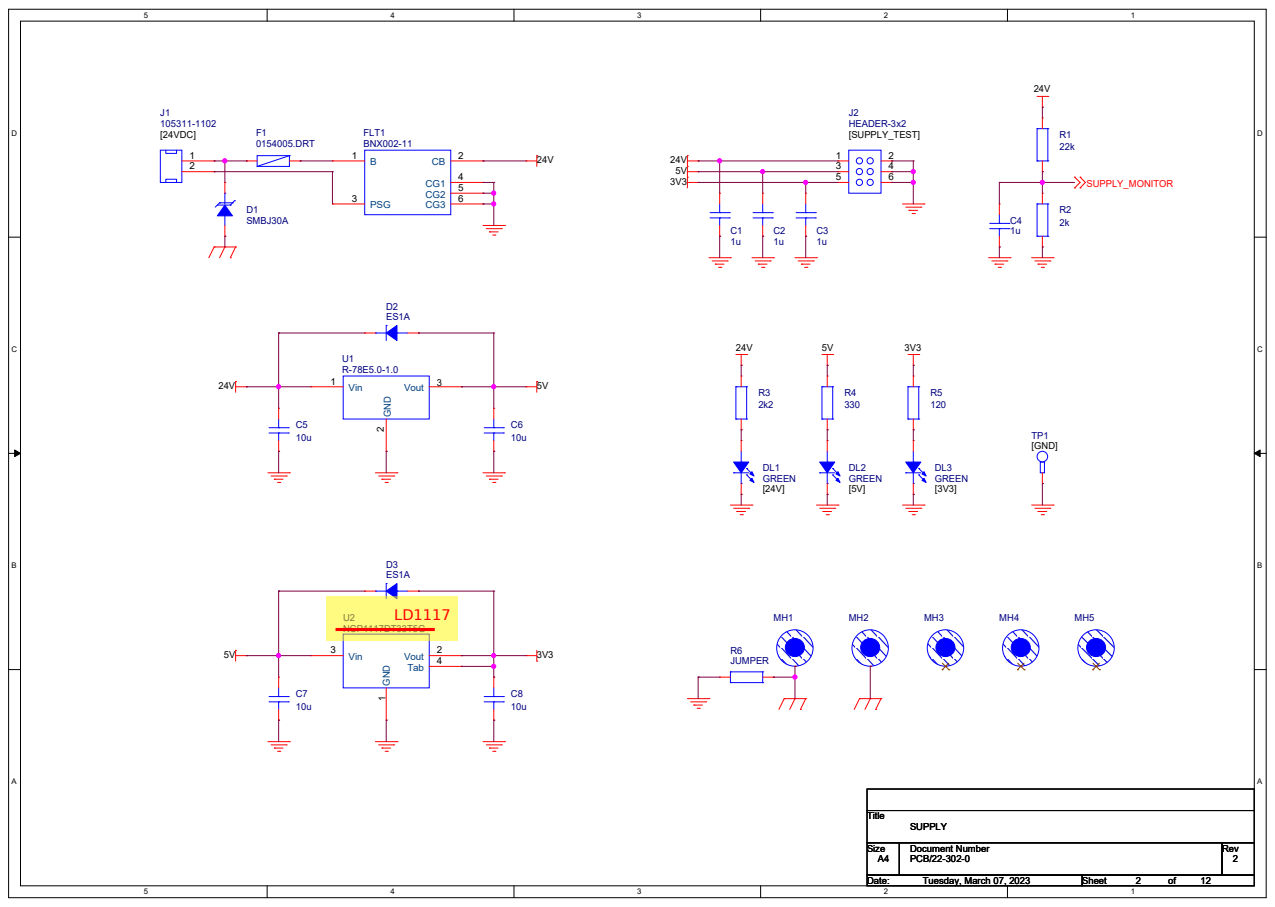
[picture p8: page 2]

VDDIO_2 48 VDDIO_3 56 | VSW ⁵⁵ | DL4 BLUE

# 32.768kHz 1 2 R8

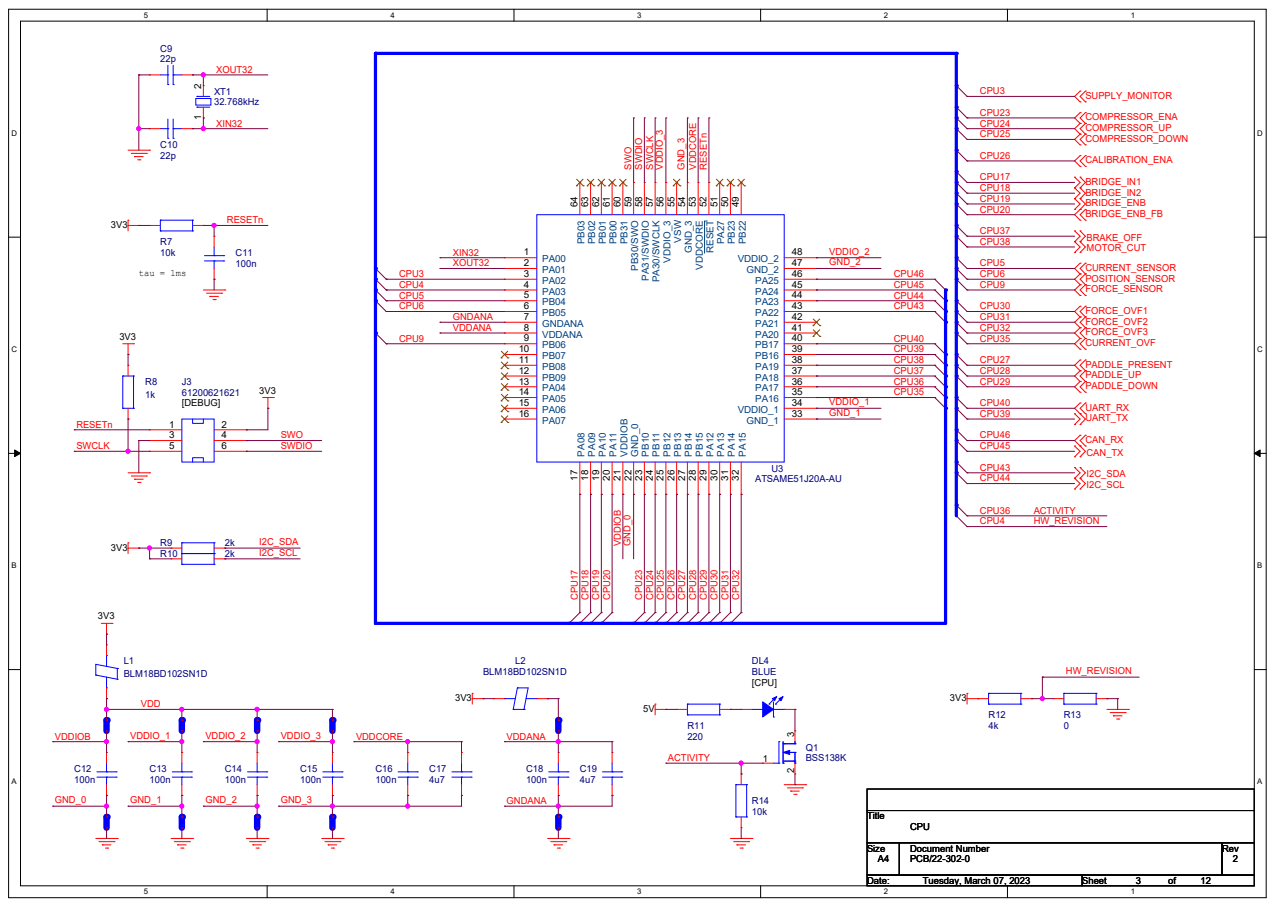
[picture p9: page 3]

PA20 41 PA21 42 PA22 43 PA23 44 PA24 45 PA25 46 PA²⁷ ⁵¹ PA³⁰/SWCLK ⁵⁷ PA³¹/SWDIO ⁵⁸ PB⁰⁰ ⁶¹ PB⁰¹ ⁶² PB⁰² ⁶³ PB⁰³ ⁶⁴

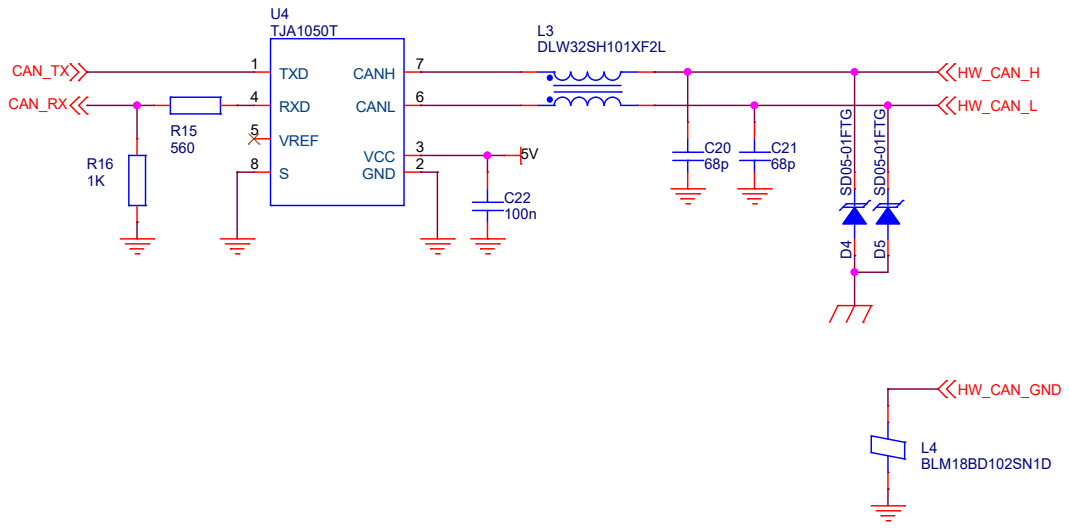
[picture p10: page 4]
CAN_TX; CAN_RX; HW_CAN_H; HW_CAN_L; HW_CAN_GND; Title; CAN BUS; Tuesday, March 07, 2023; 12 Title; U4 TJA1050T; CANH; 7 CANL 6; 8 TXD 1; VCC; D⁴ SD⁰⁵⁻⁰¹FTG R15; L4BLM18BD102SN1D; L3 DLW32SH101XF2L

GND 2 VREF 5 RXD 4 S

560 D⁵ SD⁰⁵⁻⁰¹FTG C22

## 4 x TCMT1104

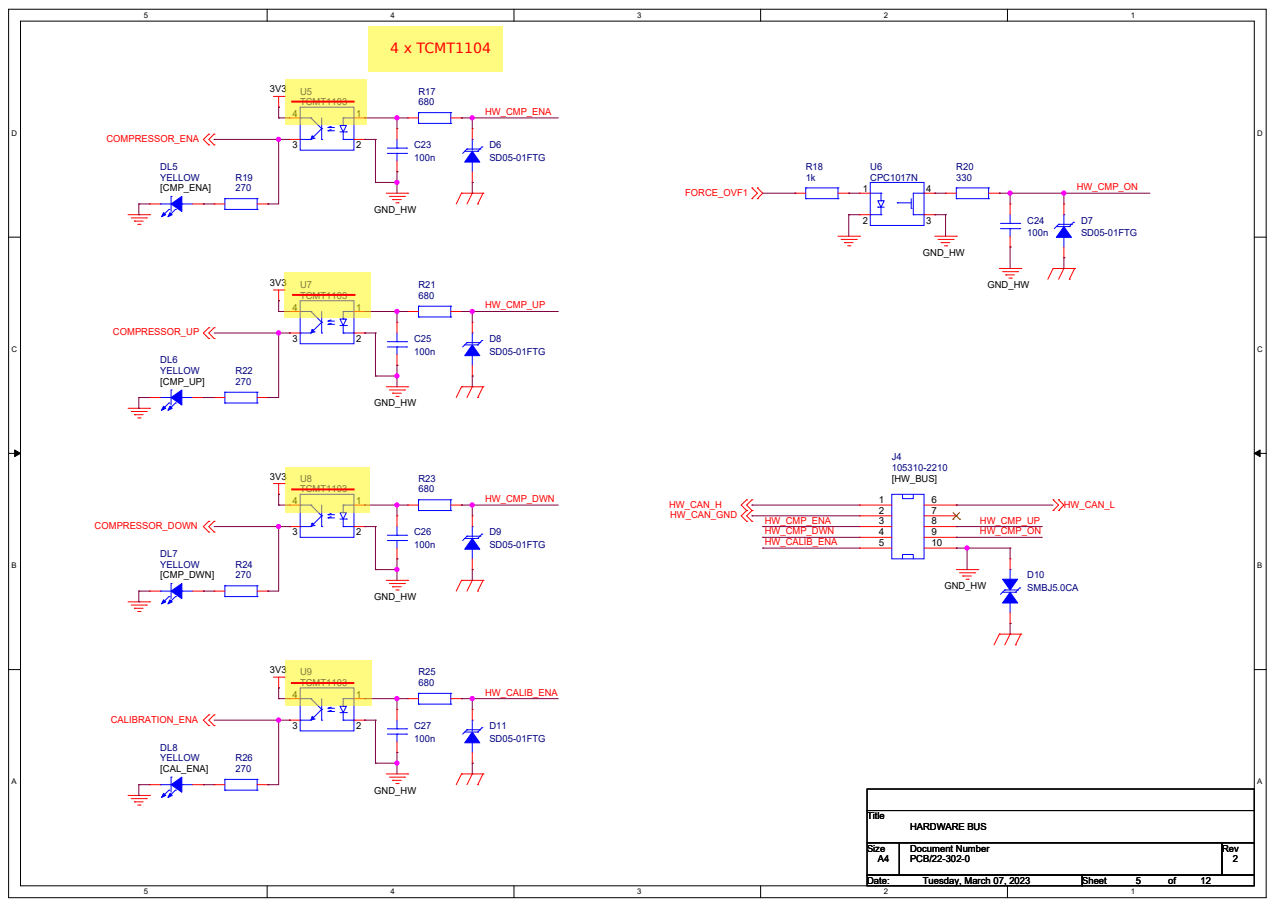
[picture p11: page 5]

-U10D

-U10A

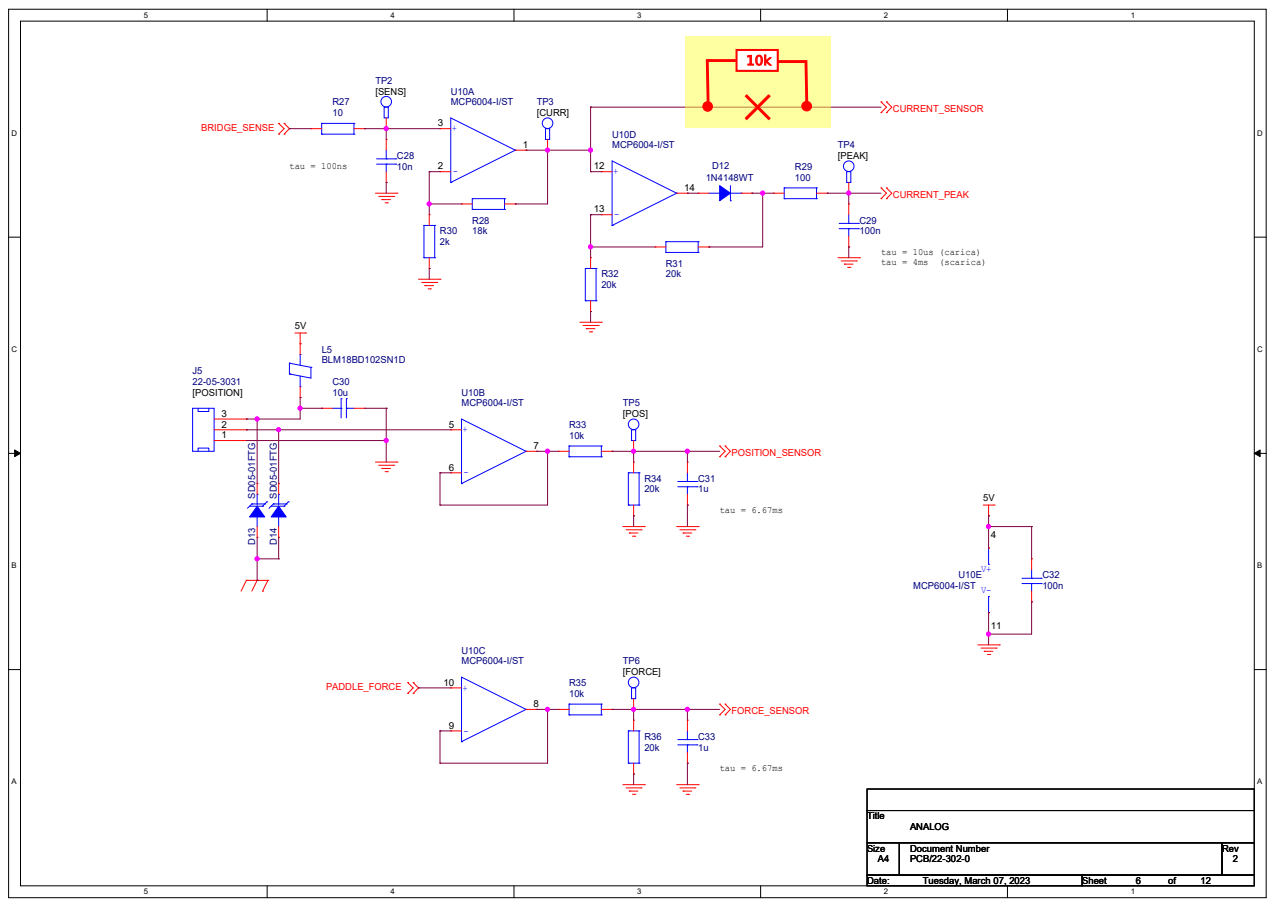
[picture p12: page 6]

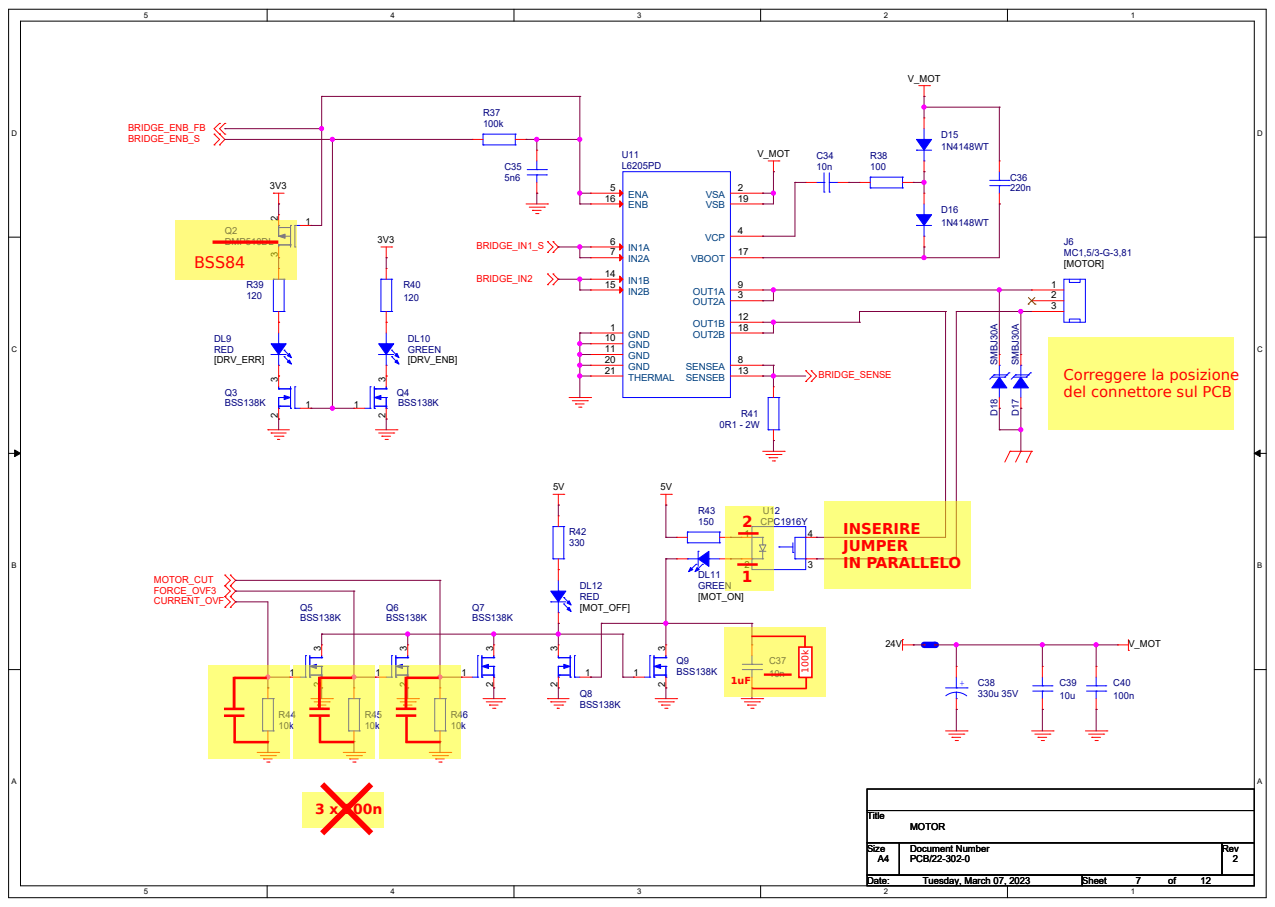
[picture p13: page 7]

Correggere la posizione
del connettore sul PCB

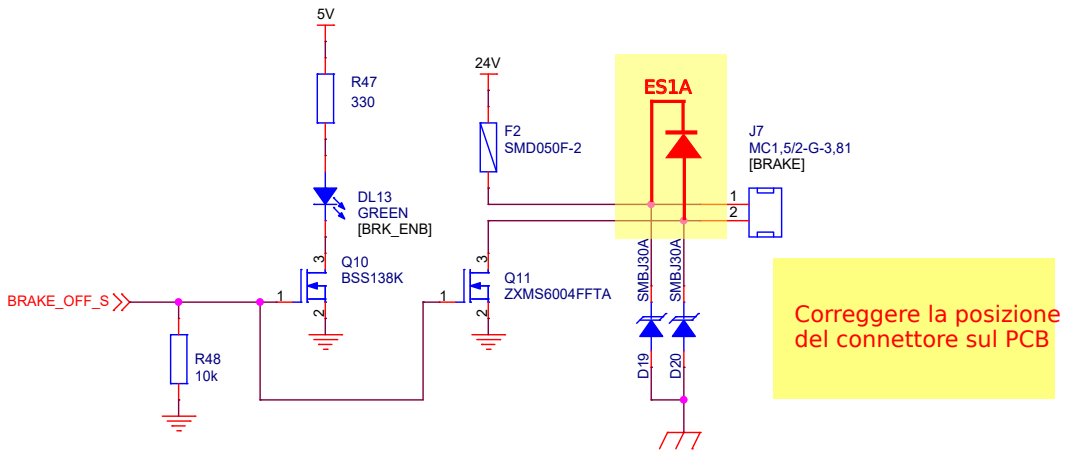
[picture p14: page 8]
BRAKE_OFF_S; Title; PCB/22-302-0; 2 BRAKE; Tuesday, March 07, 2023; D²⁰ SMBJ30A; F2SMD050F-2; Q11 ZXMS6004FFTA; Q10 BSS138K; 2 D19 SMBJ30A; J7 MC1,5/2-G-3,81 [BRAKE] 1; 2 DL13 GREEN [BRK_ENB]

Correggere la posizione
del connettore sul PCB

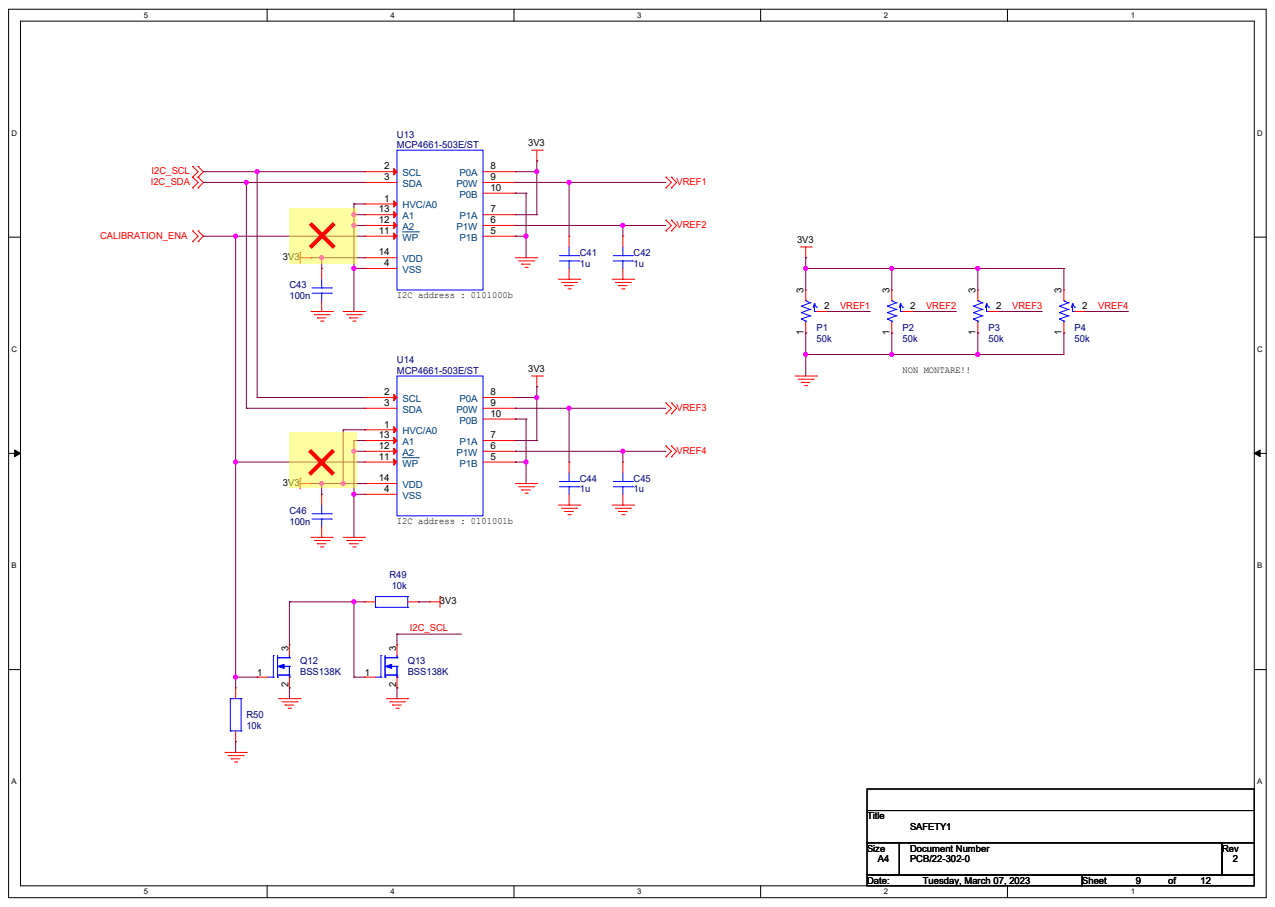
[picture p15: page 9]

-U16A

-U15A

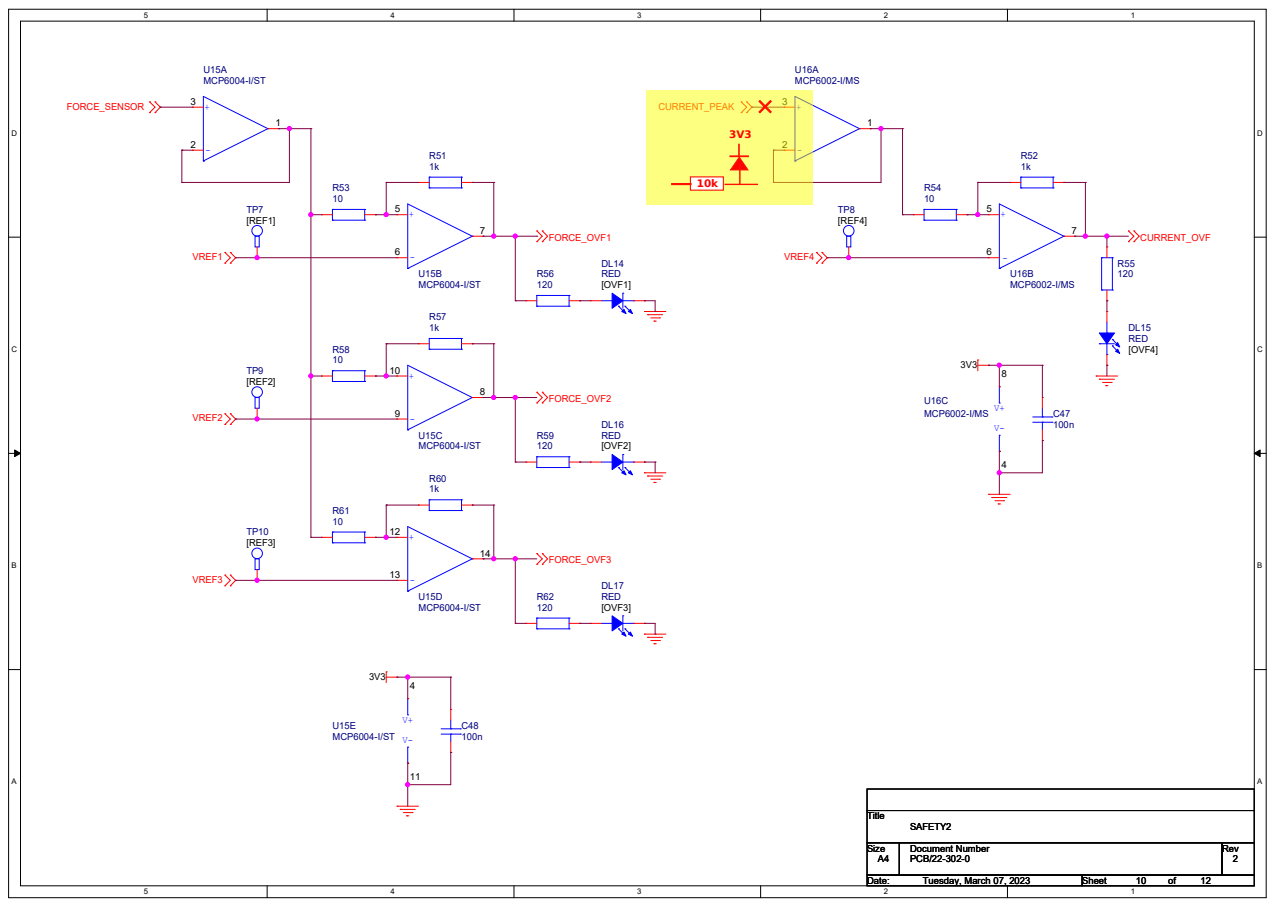
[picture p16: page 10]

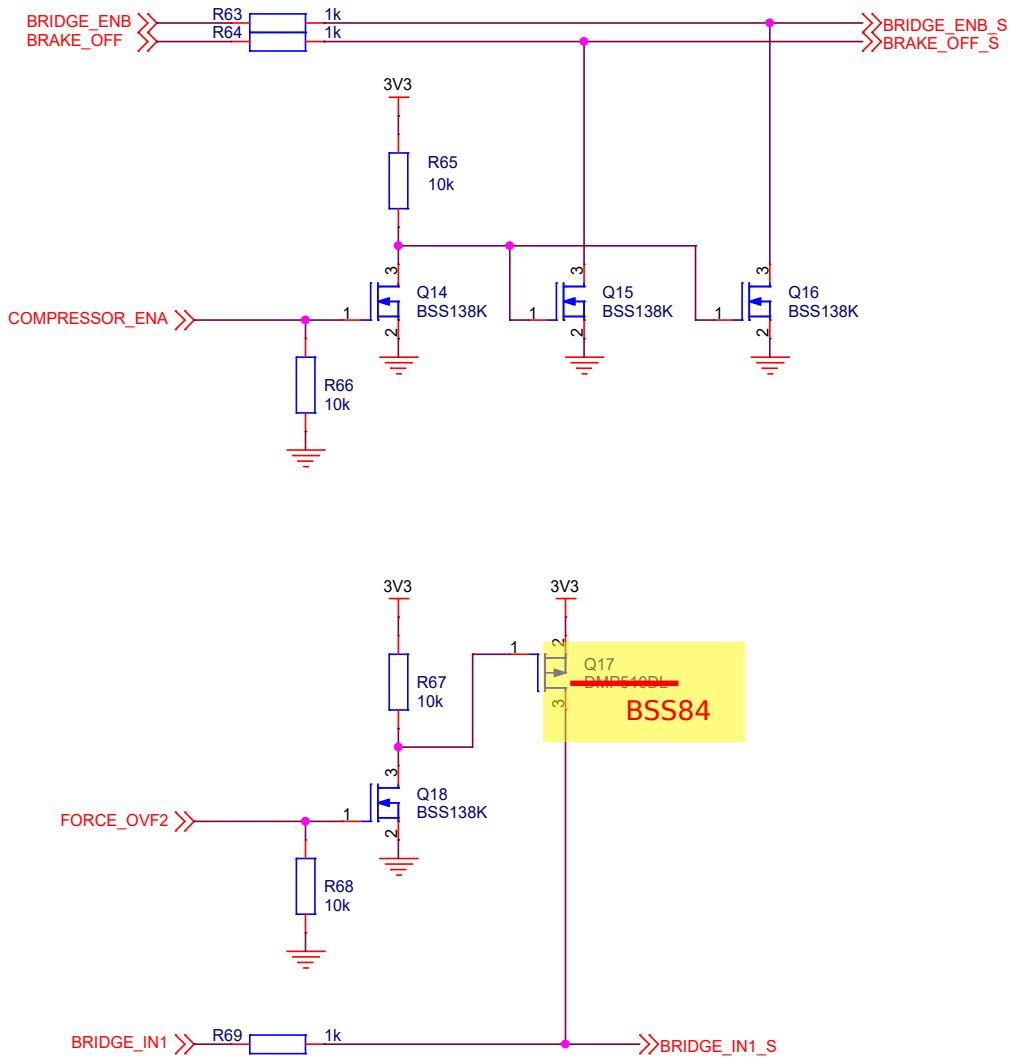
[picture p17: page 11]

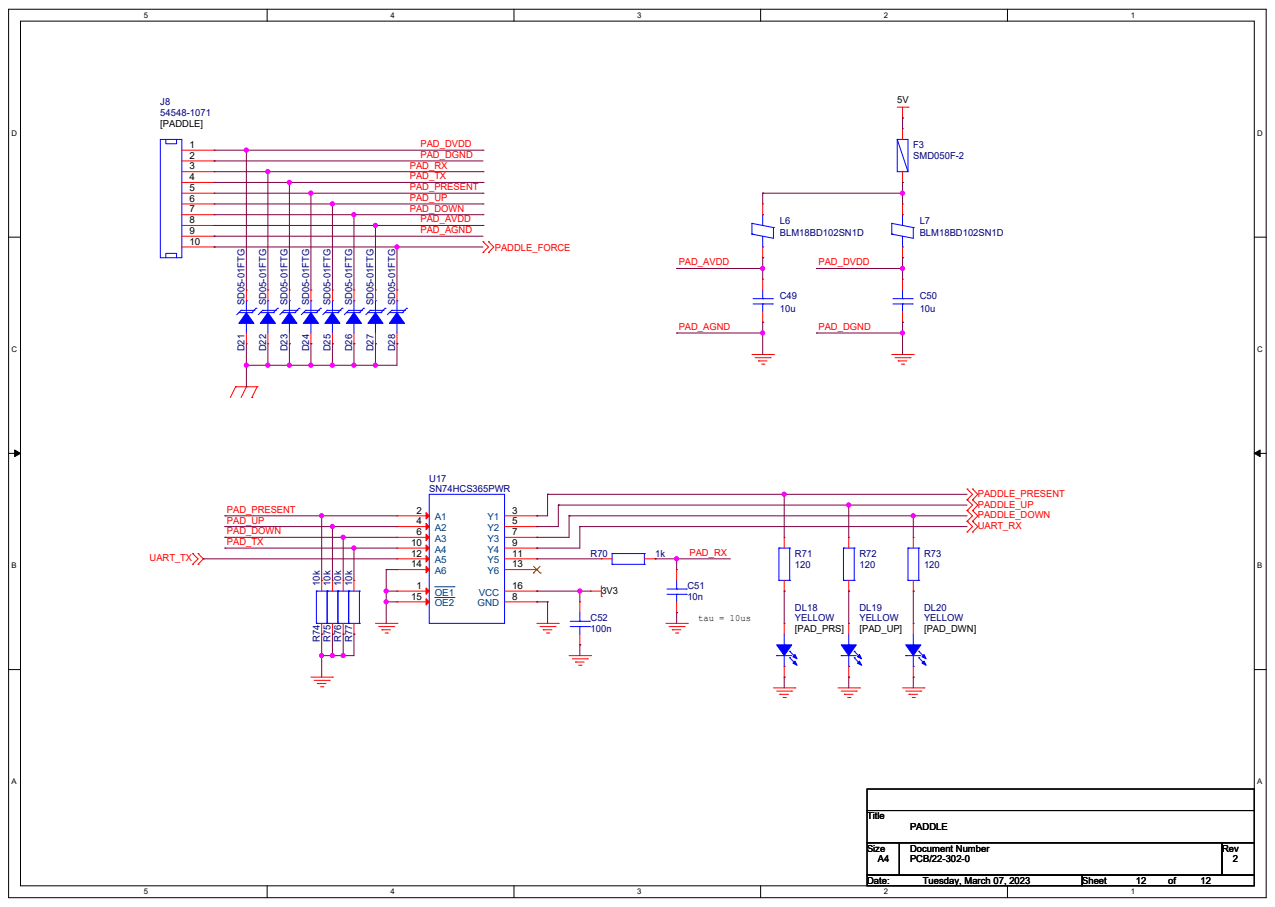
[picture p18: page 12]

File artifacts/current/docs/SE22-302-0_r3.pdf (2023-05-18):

METALTRONICA S.p.a.

# PCB/22-302-0 Scheda di controllo del compressore (DiMoBIS)


- Sostituiti i diodi D4, D5, D6, D7, D8, D9, D11, D13, D14, D21, D22,
D23, D24, D25, D26, D27, D28 con il part number SD05-01FTG.

- Inserito R78 sulla net CURRENT_SENSOR, nella pagina ANALOG
- Inserito R79 in parallelo a C37, nella pagina MOTOR
- Corretto il simbolo di U12
- Invertite le net sui pin 1 e 2 di U12
- Inserito il jumper J9 in parallelo all'uscita di U12, nella pagina MOTOR
- Inserito D29 in parallelo a J7, nella pagina BRAKE
- Disconnesso il pin 11 di U13 e U14 dalla net CALIBRATION_ENA, nella pagina
SAFETY1
- Inseriti D30 e R80 sull'ingresso di U16A, nella pagina SAFETY2
- Modificato J8 con il part number 54548-1271, a 12 contatti anziché 10
- Modificato C37 con il valore 1uF
- Modificato U2 con il part number LD1117DT33
- Modificati U5, U7, U8, U9 con il part number TCMT1104
- Modificati Q2, Q17 con il part number BSS84


# 32.768kHz 1 2 R8


PA20 41 PA21 42 PA22 43 PA23 44 PA24 45 PA25 46 PA²⁷ ⁵¹ PA³⁰/SWCLK ⁵⁷ PA³¹/SWDIO ⁵⁸ PB⁰⁰ ⁶¹ PB⁰¹ ⁶² PB⁰² ⁶³ PB⁰³ ⁶⁴

CAN_TX; CAN_RX; HW_CAN_H; HW_CAN_L; HW_CAN_GND; Title; CAN BUS; Thursday, May 18, 2023; 12 Title; U4 TJA1050T; CANH; 7 CANL 6; 8 TXD 1; VCC; D⁴ SD⁰⁵⁻⁰¹FTG R15; L4BLM18BD102SN1D; L3 DLW32SH101XF2L

GND 2 VREF 5 RXD 4 S

560 D⁵ SD⁰⁵⁻⁰¹FTG C22


-U10D

-U10A



BRAKE_OFF_S; Title; PCB/22-302-0; 3 BRAKE; Thursday, May 18, 2023; D29 ES1A D²⁰ SMBJ30A; F2SMD050F-2; Q11 ZXMS6004FFTA; Q10 BSS138; 2 D19 SMBJ30A; J7 MC1,5/2-G-3,81 [BRAKE] 1; 2 DL13 GREEN [BRK_ENB]


-U16A

-U15A






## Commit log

2022-09-08 Revisione iniziale
    [22-302-0.DSN]
2022-12-07 Inseriti datasheet
    [motors.xlsx, sensors.xlsx]
2022-12-07 Inseriti progetti di simulazione
2022-12-07 Aggiornato il progetto dello schematico
    [22-302-0.DSN]
2022-12-07 Generati artefatti della documentazione
    [LP22-302-0_r1.xlsx]
2022-12-16 Aggiornato il documento di progettazione
2023-03-02 Archiviato il rilascio del master definitivo.
2023-03-02 Aggiornate le note di sbroglio rilasciate.
2023-03-02 Acquisite le modifiche allo schematico dal masterista.
    [22-302-0.DSN]
2023-03-02 Acquisito il progetto del layout dal masterista.
2023-03-02 Acquisiti gli artefatti del layout dal masterista.
    [22-302-0.DRL, 22-302-0.dwg, PF22-302-0.dwg, PM22-302-0.dwg]
2023-03-02 Rinominata la cartella orcad in capture.
    [22-302-0.DSN]
2023-03-07 Ripristinato il progetto dello schematico proprietario.
    [22-302-0.DSN]
2023-03-07 Inserita la proprietà 'PCB Footprint' nella BOM.
2023-03-07 Sostituiti alcuni TVS con versioni meno ingombranti.
    Aggiornate le informazioni relative ai footprint dei componenti.
    [22-302-0.DSN]
2023-03-08 Aggiornati gli artefatti di schematico e lista parti.
    [LP22-302-0_r1.xlsx, LP22-302-0_r2.xlsx]
2023-03-08 Aggiornata la documentazione di progetto.
2023-05-15 Creato schematico schedina di test.
    [TESTER.DSN]
2023-05-16 Creata la revisione 3 dello schematico.
    [22-302-0.DSN]
2023-05-16 Aggiornati gli artefatti della documentazione.
    [LP22-302-0_r2.xlsx, LP22-302-0_r3.xlsx]
2023-05-18 Sostituito il connettore J8 con un connettore da 12 linee anziché 10.
    [22-302-0.DSN, LP22-302-0_r3.xlsx]
2023-05-18 Aggiornate modifiche pcb.
2023-06-05 Archiviato il rilascio del master modificato.
    [22-302-0.DRL, 22-302-0.DSN, 22-302-0.dwg, PF22-302-0.dwg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]
